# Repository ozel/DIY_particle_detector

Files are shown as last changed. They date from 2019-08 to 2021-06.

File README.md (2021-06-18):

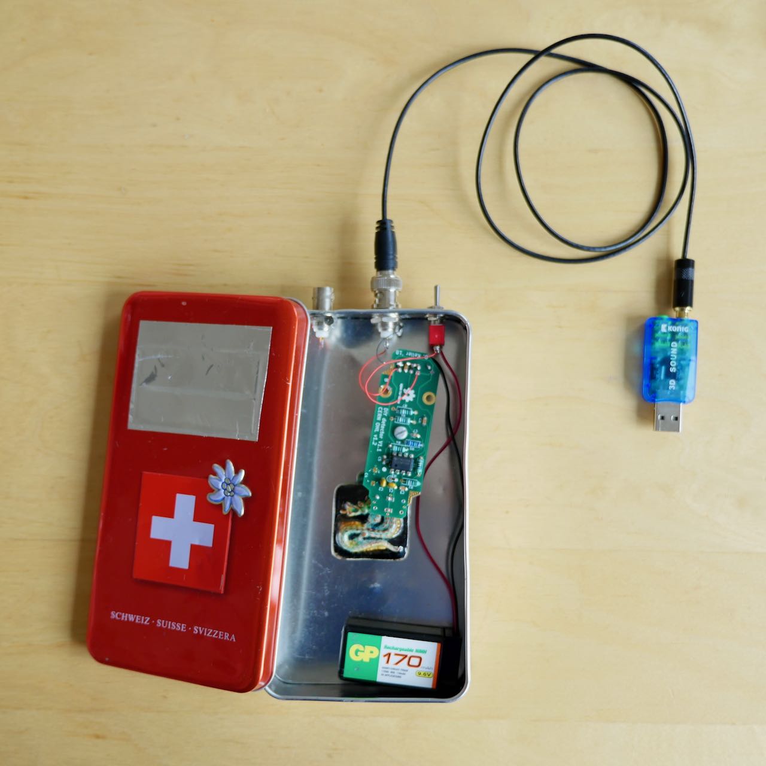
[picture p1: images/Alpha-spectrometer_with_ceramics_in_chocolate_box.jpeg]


*Corresponding scientific article:* 

*Repository archive on Zenodo:* 

# DIY Particle Detector

**Short summary video on twitter**<br>
:point_right: https://twitter.com/CERN/status/1260600298206302210

A mobile low-cost spectrometer for measuring ionising radiation like alpha particles and electrons (energy range: 33 keV to 8 MeV).   
It's an experimental educational tool and citizen science device made for exploring natural and synthetic sources of radioactivity such as stones, airborne radon, potassium-rich salt or food and every-day objects (Uranium glass, ceramics, old Radium watches etc.).

<u>*The main project documentation can be found in **[the Wiki](https://github.com/ozel/DIY_particle_detector/wiki)**.*</u>   

A summary of the main aspects can be found below.    
The hardware design and documentation is licenced under the [CERN Open Hardware License](https://github.com/ozel/DIY_particle_detector/blob/master/hardware/V1.2/CERN_OPEN_HARDWARE_LICENSE_OHL_v_1_2.txt).   
The open source software is provided under the terms of the [BSD licence](https://github.com/ozel/DIY_particle_detector/blob/master/LICENSE).

This project received funding and support by [CERN](http://home.cern) and the [Fellow FreiesWissen program](https://github.com/ozel/DIY_particle_detector/wiki/Fellow-FreiesWissen-Project).

 &#8195;    

***Project Overview:***
* [How does it work?](#how-does-it-work)
* [Hardware](#hardware)
    * [Two variants](#detector-variants): Electron-Detector (easier, lower costs) and Alpha-Spectrometer (more advanced)
    * [General requirements](#general-requirements)
    * [Detector signals](#detector-signals)
* [Software](#software) for recording and analysing measurements
* [Reference measurements and plots](#reference-measurements-and-plots)
* [Workshops](#workshops) with high-school students, teachers and makers

*Much more detailed information is available in **[the project Wiki](https://github.com/ozel/DIY_particle_detector/wiki)**.*     

## How does it work?
Tiny amounts of electrical charge are generated in repurposed photodiodes by impinging particles. The charges form currents which are amplified and converted into voltage pulses that are compatible with audio/microphone signal inputs.
The size of the pulse is proportional to the energy deposited by the ionising radiation. A reference calibration with sources of known energy spectra is provided.

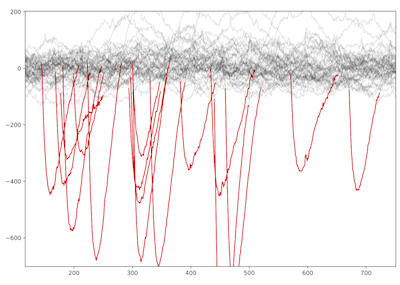
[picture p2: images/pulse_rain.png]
<br><br>

A superposition of several recorded pulse waveforms from electrons of beta decays (KCl salt sample, more info below) is shown on the right. This is the raw analog ouput signal of the detector.

Black lines in the upper area represent electronic noise, detected signal pulses from the natural radioactivity of potassium (isotope K-40) are highlighted in red.

<br>

<br>

<br>

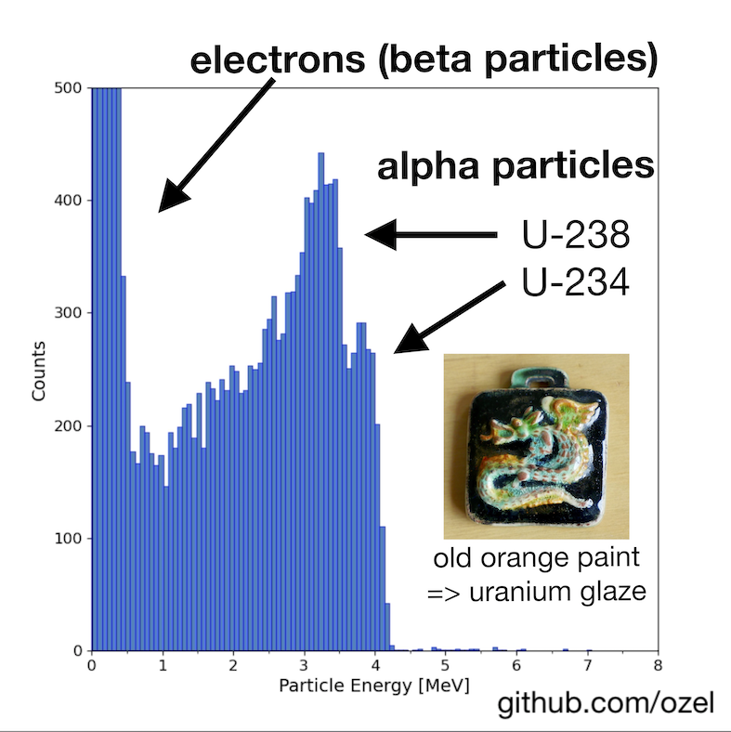
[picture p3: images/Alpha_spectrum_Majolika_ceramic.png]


The energy spectrum on the right - derived from the size of signal pulses - was taken from an old ceramics pendant of the Majolika manufacture (Karlsruhe/Germany) - without vacuum pump, in normal ambient air! 

The characteristic alpha energies of the uranium isotopes are about 1 MeV lower than the actual values due to internal absorption caused by the transparent surface coating on top of the orange uranium-based glaze. More details on the energy calibration below and in the [paper](https://doi.org/10.3390/s19194264).

<br>

<br>

## Hardware

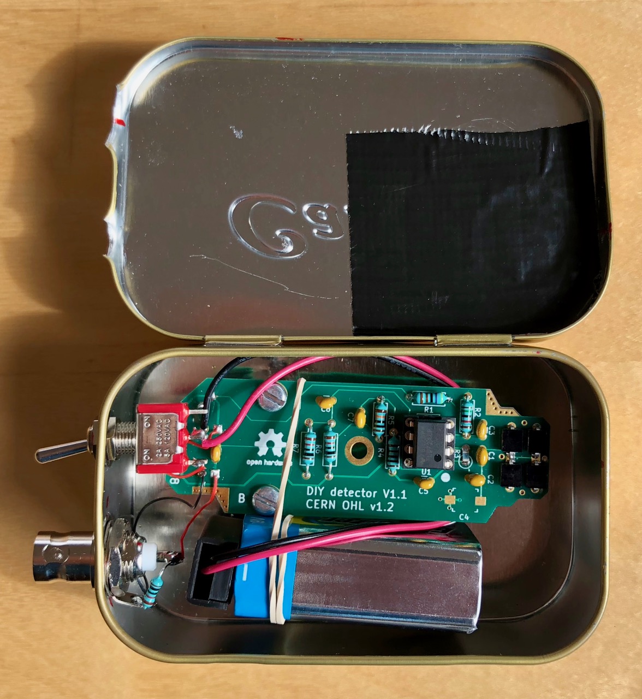
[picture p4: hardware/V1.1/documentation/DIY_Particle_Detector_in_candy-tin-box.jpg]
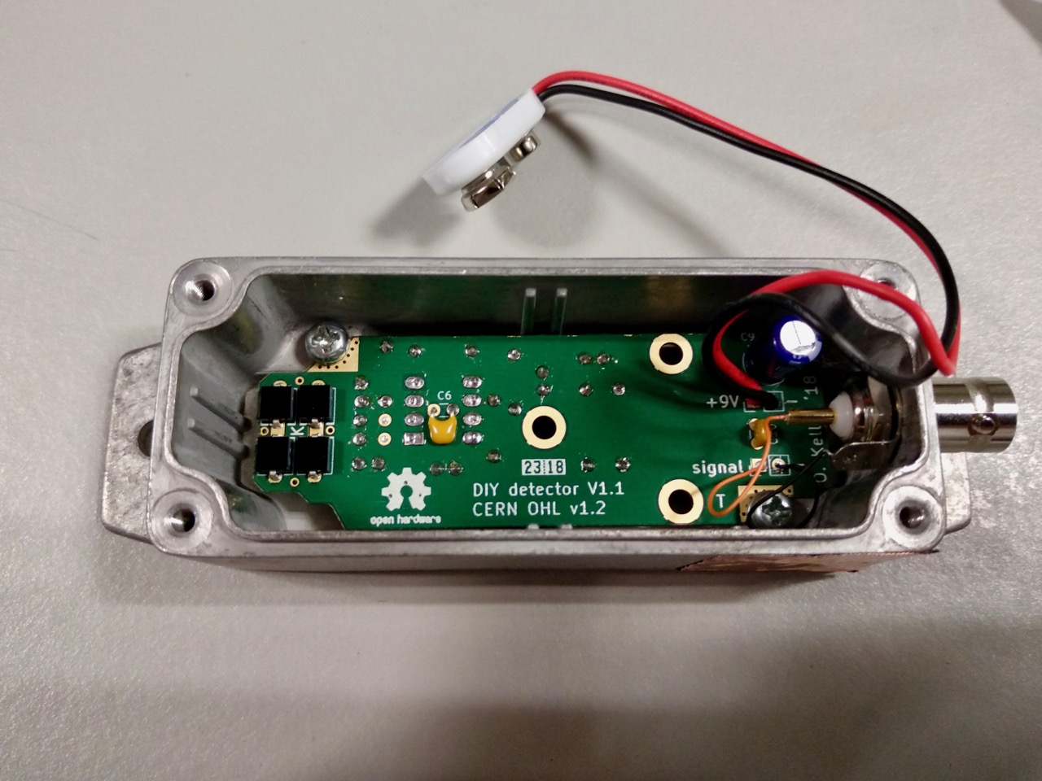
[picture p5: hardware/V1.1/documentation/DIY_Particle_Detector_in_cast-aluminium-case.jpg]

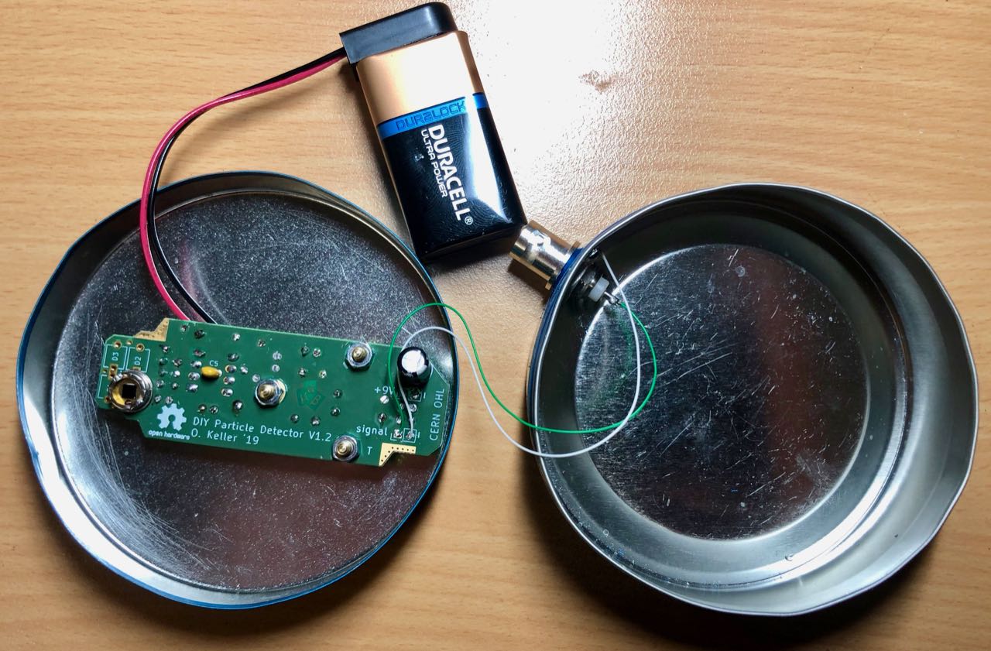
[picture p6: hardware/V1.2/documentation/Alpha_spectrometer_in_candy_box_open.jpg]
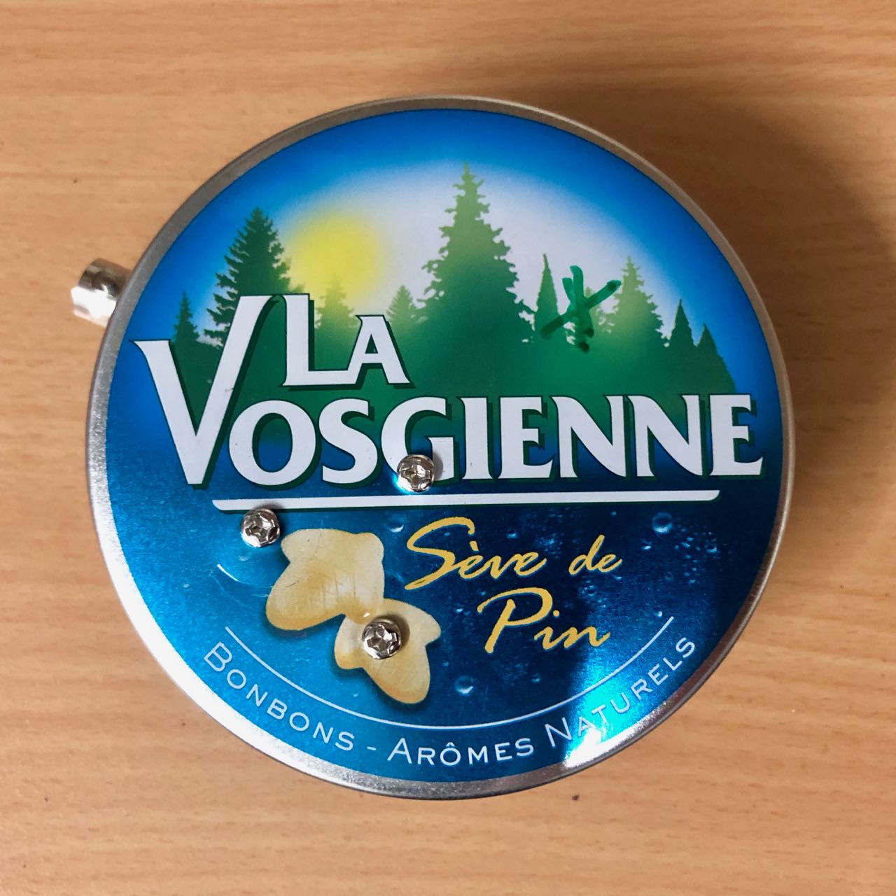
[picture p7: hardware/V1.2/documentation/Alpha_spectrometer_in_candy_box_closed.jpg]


More photos of finished builds from users around the world can be found in the [picture gallery](https://github.com/ozel/DIY_particle_detector/wiki/Gallery).     
The open hardware design in this repository is released under the terms of the CERN Open Hardware Licence V1.2.
Usage guidelines and legal requirements for users of this license can be found [here](https://ohwr.org/project/cernohl/wikis/Documents/CERN-OHL-version-1.2).
### Detector Variants
The same circuit board is used with two partially different sets of components in two assembly variants.
For electronic beginners, starting with the electron-detector version is *highly recommended* over the alpha-spectrometer.

* ***Alpha-spectrometer*** measuring energies of alpha particles and electrons using one BPX61 diode.<br/>
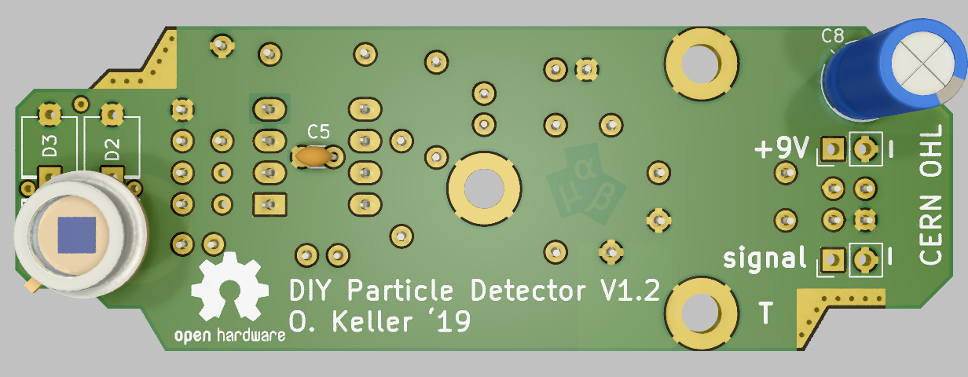
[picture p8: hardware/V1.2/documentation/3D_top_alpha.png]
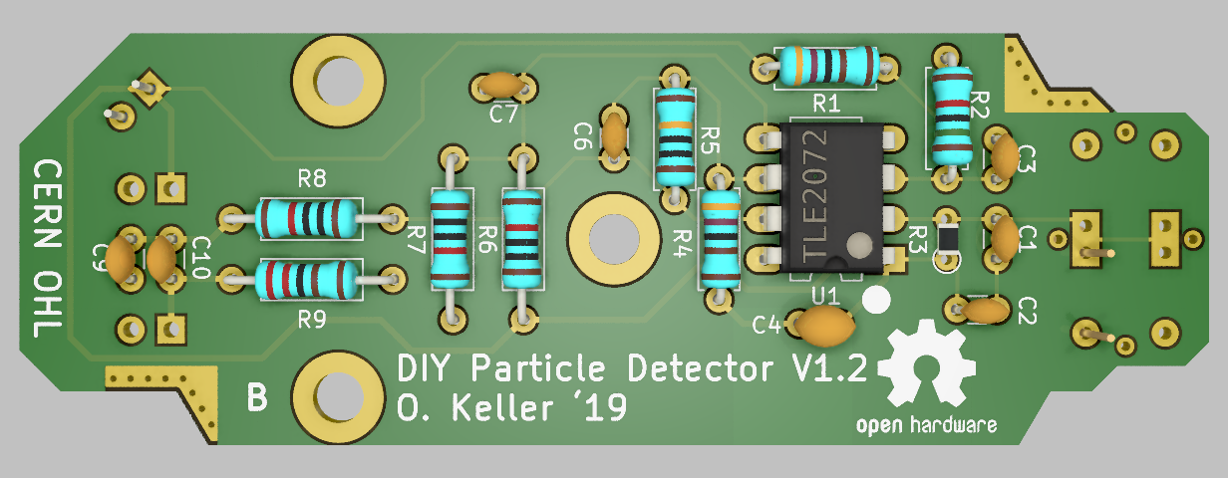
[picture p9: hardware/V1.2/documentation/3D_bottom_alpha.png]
  <br/>
  After the glass window of the diode is carefully broken-up and removed, it can sense alpha particles (see close-up pictures in the [wiki](https://github.com/ozel/DIY_particle_detector/wiki/Diodes#preparation-of-the-bpx61-diode-for-alpha-spectroscopy). 
  The circuit works most precise with only one BPX61 diode (lowest electronic noise) and was specificaly tuned for this scenario.
  * [get alpha-spectrometer parts & circuit board via kitspace](https://kitspace.org/boards/github.com/ozel/diy_particle_detector/diy%20alpha%20spectrometer/)
  * [short parts overview & assembly guide for the alpha-spectrometer](https://raw.githubusercontent.com/ozel/DIY_particle_detector/master/hardware/V1.2/documentation/DIY%20detector%20-%20parts%20overview%20v1-2%20alphaspectrometer%20version.pdf)
  * [detailed assembly instructions and list of required tools](https://github.com/ozel/DIY_particle_detector/wiki/Assembly-Instructions)
  * [scientific article incl. reference energy calibration with alpha sources](https://doi.org/10.3390/s19194264)

* ***Electron/beta radiation detector*** measuring mostly electrons (plus few gamma photons) with four very low-cost BPW34F or BPW34FA diodes (<1 EUR each).<br/>
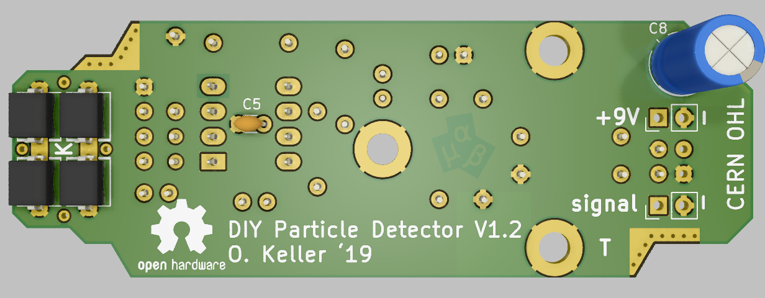
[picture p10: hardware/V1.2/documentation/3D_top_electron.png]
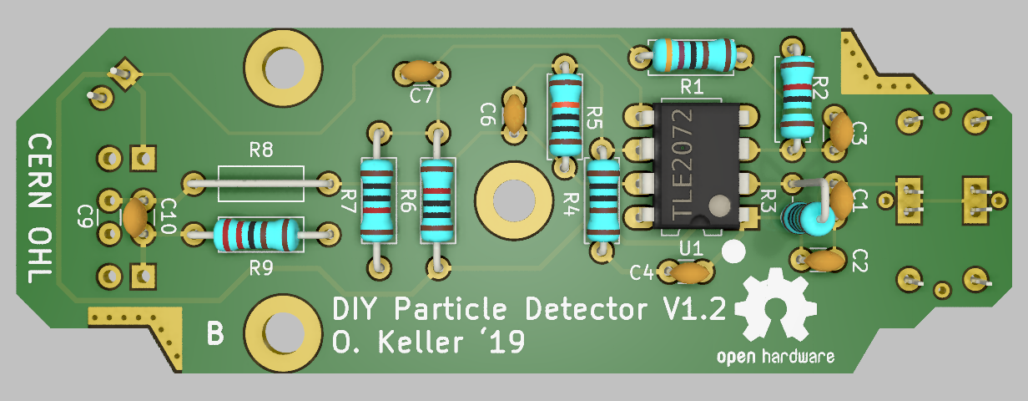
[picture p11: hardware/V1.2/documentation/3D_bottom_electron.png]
  <br/>
  This variant is not able to detect alpha particles but is  easier to operate (less sensitive to visible light and electromagnetic interference, see section on general requirements below). It is also more sensitive towards sources of low intensity (low rate of radioactive decays) since it has four times the sensor volume compared to using only one diode as sensor. This version is ideal for beginners, in total only 8 components are different compared to the alpha-spectrometer variant above. This variant is similar to the previous circuit version 1.1.
  * [get electron-detector parts & circuit board via kitspace](https://kitspace.org/boards/github.com/ozel/diy_particle_detector/diy%20electron%20detector/)
  * [short parts overview & assembly guide for the electron-detector](https://raw.githubusercontent.com/ozel/DIY_particle_detector/master/hardware/V1.2/documentation/DIY%20detector%20-%20parts%20overview%20v1-2%20electron%20version.pdf) 
  * [detailed assembly instructions and list of required tools](https://github.com/ozel/DIY_particle_detector/wiki/Assembly-Instructions)

Both kinds of diodes, the BPW34 series in various plastic cases and the BPX61 with metal casing, have the same sensitive area (~7 mm^2). The physics of these sensors when used with ionizing radiation is explained in detail in the [article corresponding to this repository](https://doi.org/10.3390/s19194264). The section about figure 1 discusses why their efficiency for detecting gamma photons is quite low in general.  

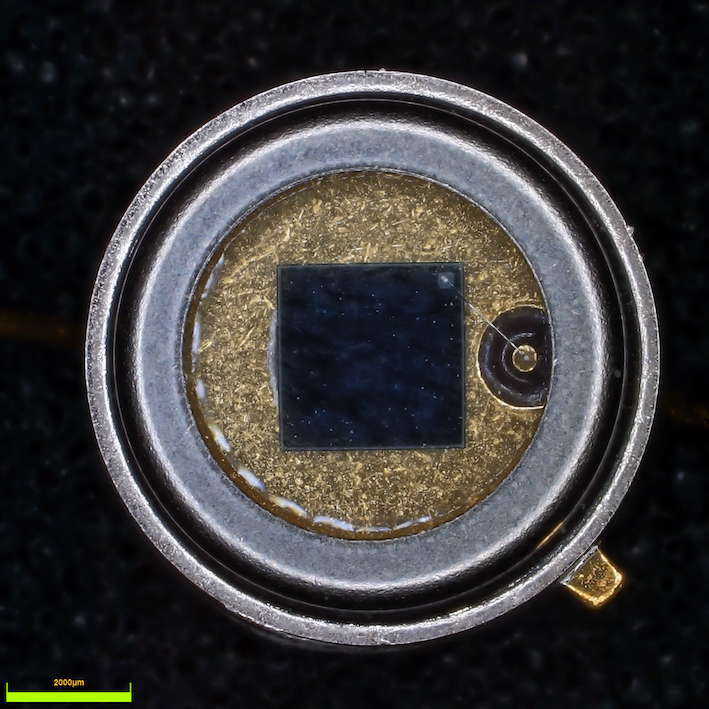
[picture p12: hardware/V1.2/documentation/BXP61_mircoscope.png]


Mircoscope image of the Osram BPX61 diode on the left, the green scale indicates 2 mm. The sensitive area of the silicon chip is 2.65 x 2.65 mm^2. A bond wire from the anode pin on the right connects the top of the silicon chip (this side is also marked with a notch in the metal case, lower right corner). For detecting alpha particles, the glass window of this diode must be removed.    
Further instructions in the [wiki](https://github.com/ozel/DIY_particle_detector/wiki/Diodes).

<br>

<br><br>

<br><br>

### General Requirements

* An absolutely light-tight and electromagnetically shielding metal case is mandatory. Either a commercial one made of die casted aluminium (thick metal provides better immunity towards vibrations and prevents "microphonic effects") or an upcycled tin box for candies. Detailed recommendations in the [wiki](https://github.com/ozel/DIY_particle_detector/wiki/Enclosures).
* 9 V [battery](https://github.com/ozel/DIY_particle_detector/wiki/Batteries). NIMH-type accumulators with a nominal value of 9.6 V work best (mains-connected power supplies would introduce too much noise, always use batteries if building the detector for the first time!)
* Signal output is in the range of +/- 0.1 V and compatible with an audio/microphone input such as a [headset connector](https://github.com/ozel/DIY_particle_detector/wiki/Cables#connection-with-a-headset-socket) of a mobile phone or laptop (or an oscilloscope if available)
* The alpha-spectrometer should be operated using a low-cost USB soundcard for best results, see the [wiki](https://github.com/ozel/DIY_particle_detector/wiki/Soundcards).
* The connection cable should be shielded and not too long, recommendations in the [wiki](https://github.com/ozel/DIY_particle_detector/wiki/Cables). 

### Detector Signals
Typical signals from the electron-detector (left/top) and alpha-spectrometer (right/bottom) on an oscilloscope:
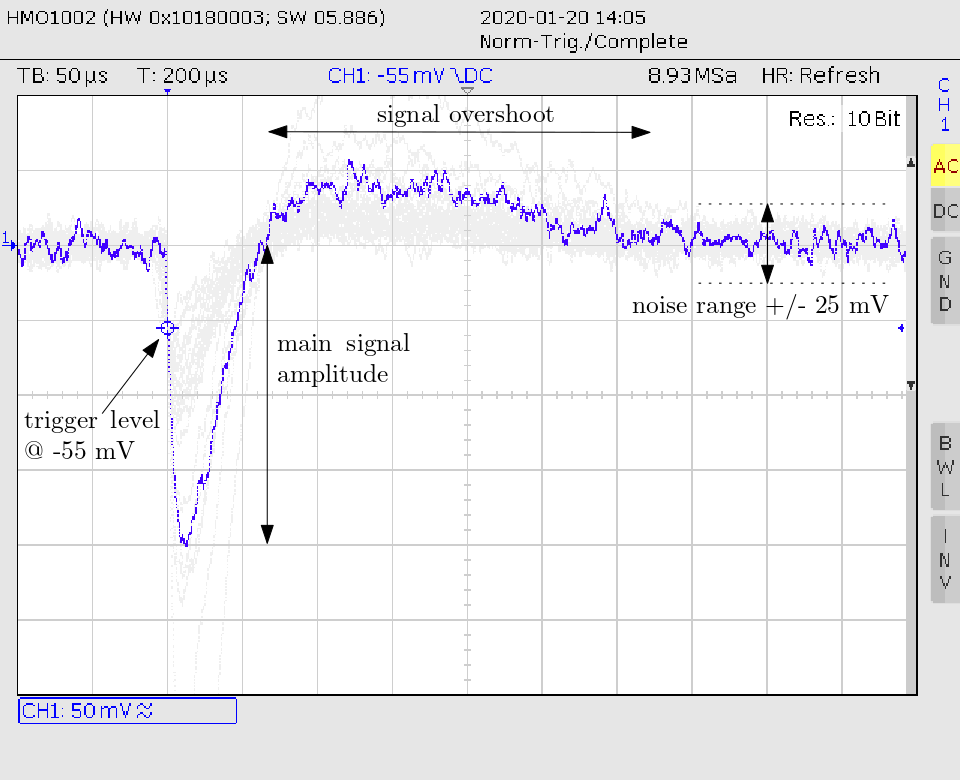
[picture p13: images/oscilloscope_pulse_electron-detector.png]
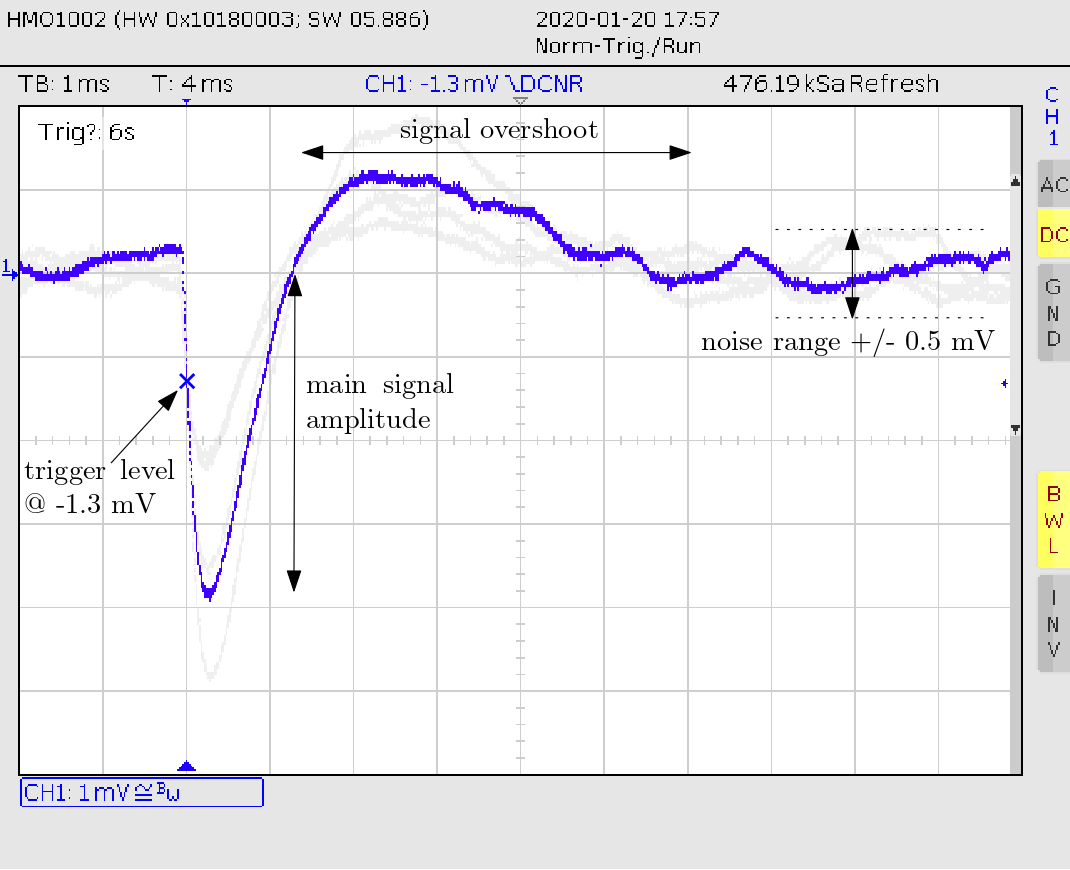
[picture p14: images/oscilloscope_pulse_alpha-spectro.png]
      
More details in the [wiki](https://github.com/ozel/DIY_particle_detector/wiki/Oscilloscope-Measurements).

## Software
The open source software in this repository is provided under the terms of the BSD Licence.

It consists of two parts (links to the wiki):
* [Recording, real-time display and counting of particle pulses](https://github.com/ozel/DIY_particle_detector/wiki/Software#signal-display--pulse-counting)     
  Different softwares for desktop computers as well as mobile devices are decsribed in the wiki.     
  Most universal is a [web browser application](https://ozel.github.io/DIY_particle_detector/data_recording_software/webGui/) based on the Web Audio API available in modern browsers (recent Chrome and Firefox versions work best):     
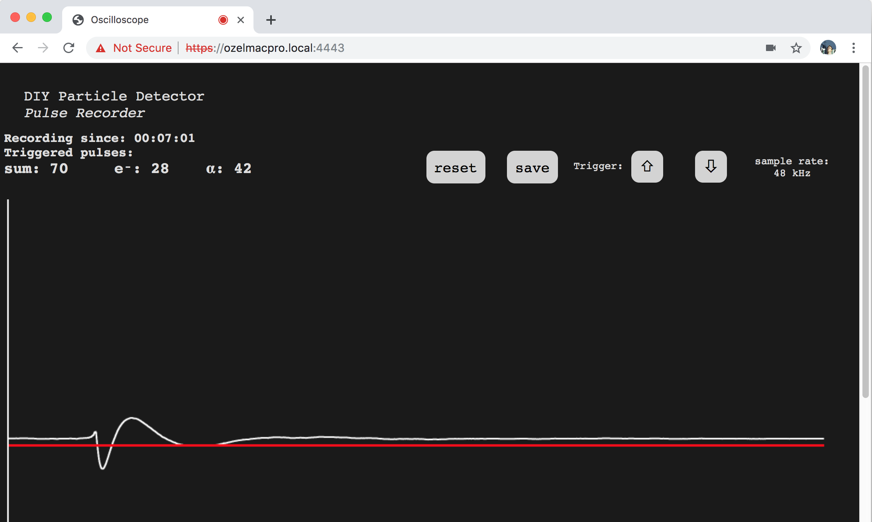
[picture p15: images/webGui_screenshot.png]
A single pulse recorded by the web browser GUI.
        
  This acts essentially as a software oscilloscope with trigger functionality (red line = trigger level) reading small detector pulses directly from the microphone input or headset socket of a computer or mobile device.

* [Data analysis of alpha-spectrometer measurements](https://github.com/ozel/DIY_particle_detector/wiki/Software#energy-spectra-from-alpha-particles), providing calibrated energy spectra and time series histograms

## Reference measurements and plots

Several reference measurements have been taken and stored in [data_analysis_and_reference_measurements/diode_detector/data](https://github.com/ozel/DIY_particle_detector/tree/master/data_analysis_and_reference_measurements/diode_detector/data). All have been recorded using the very low-cost [CM108 USB soundcard](https://github.com/ozel/DIY_particle_detector/wiki/Soundcards), sampling the input signal @ 48 kHz and 16-bit resolution.     
*If this whole respoitory is cloned using git, the [git LFS](https://help.github.com/en/articles/duplicating-a-repository#mirroring-a-repository-that-contains-git-large-file-storage-objects) extension must be used to get as well the large data files (~ 1 GB).*
Alternatively, the data files can be downloaded from this [Zenodo data archive](https://doi.org/10.5281/zenodo.3361764).

Overview on reference measurements:

* A mixed alpha source featuring Gd-148, Pu-239, Am-241 & Cm-244 with a combined alpha energy spectrum of 3 to 6 MeV
* 10 g of KCl (potassium chlorid) salt (an alternative to NaCl table salt) as an example for detection of electrons from beta-decays (from naturally occuring K-40)
* a small columbite stone (containing trace amounts of uranium ore), a combined source of electrons and alphas (and gamma photons which do not interact enough within the thin diode detector to be relevant)
* a watch hand from an old watch that was painted with luminescent radium paint. Featuring Ra-226 and all it's radioactive progeny isotopes

## Workshops

These DIY particle detectors have been built by high school students (age 16 - 18), teachers, makers, and citizen science enthusiasts (age ~20 - 60) during several workshops.
After a little introduction into the soldering of electronic components, the whole device can be built in less than two hours - including the modification of a candy tin box as its case.

* [S'Cool LAB Summer Camp 2017](https://indico.cern.ch/event/570855/timetable/) at CERN, [poster presentation](https://indico.cern.ch/event/570855/contributions/2616929/attachments/1504724/2344411/RG3_DIY_Detector.pdf)
* [Student Summer School of Barcelona Technoweek 2017](http://icc.ub.edu/congress/TechnoWeek2018/outreach_EN.php), [CERN news](https://home.cern/news/news/knowledge-sharing/summer-school-secondary-students-spain)
* [S'Cool LAB Summer Camp 2018](https://indico.cern.ch/event/726779/timetable/) at CERN, [poster presentation, page 3](https://indico.cern.ch/event/726779/contributions/2991390/attachments/1697186/2732121/pdfjoiner.pdf)
* [Gathering of Open Science Hardware 2018 in Shenzhen China](http://openhardware.science/gatherings/gosh-2018-2/), [workshop documentation](https://forum.openhardware.science/t/day-3-build-your-own-particle-detector-discover-natural-radioactivity/1468)

*Notes and announcements of future workshops can be found in the **[Wiki](https://github.com/ozel/DIY_particle_detector/wiki)**.*     

---

The [Pixel Detector](https://github.com/ozel/DIY_particle_detector/wiki/Pixel-Detectors) and [Diode Characterisation](https://github.com/ozel/DIY_particle_detector/wiki/Diode-Characterisation) sections have been moved to the [wiki](https://github.com/ozel/DIY_particle_detector/wiki) of this project. Both are related to the [scientific article](https://www.mdpi.com/1424-8220/19/19/4264/htm) and represent supplementary material.

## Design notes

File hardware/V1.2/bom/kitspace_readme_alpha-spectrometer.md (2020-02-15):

# DIY Particle Detector
## Alpha-Spectrometer Variant

This open hardware project is a mobile low-cost spectrometer for measuring ionising radiation like alpha particles and electrons (energy range: 33 keV to 8 MeV).
It's an educational tool and citizen science device made for exploring natural and synthetic sources of radioactivity such as stones, airborne radon, potassium-rich salt or food and every-day objects (Uranium glass, old Radium watches etc.).

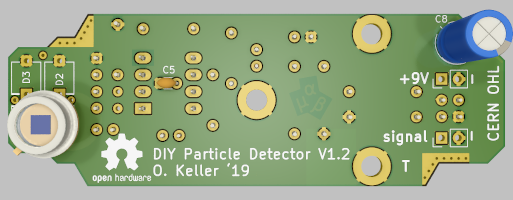
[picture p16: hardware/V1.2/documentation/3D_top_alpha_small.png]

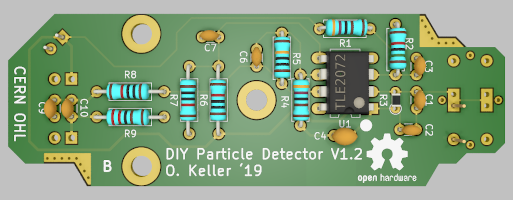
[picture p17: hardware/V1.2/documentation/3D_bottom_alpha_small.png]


[Parts overview and assembly guide](https://github.com/ozel/DIY_particle_detector/blob/master/hardware/V1.2/documentation/DIY%20detector%20-%20parts%20overview%20v1-2%20alphaspectrometer%20version.pdf)

The other [electron-detector variant](https://kitspace.org/boards/github.com/ozel/diy_particle_detector/diy%20electron%20detector/) of this project is easier to operate but cannot measure alpha particles.
Both versions of the DIY Particle Detector are using the same circuit board with different sets of components.

Please refer to the [main project description](https://github.com/ozel/DIY_particle_detector/) for further details.

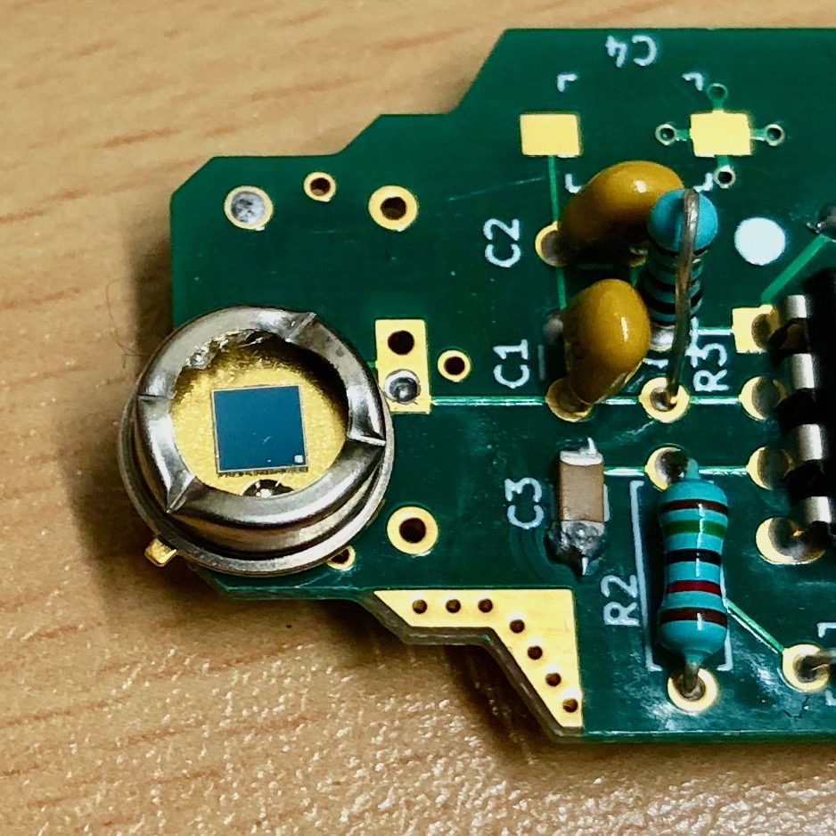
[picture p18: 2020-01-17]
hardware/V1.2/documentation/BPX61_onboard.jpg

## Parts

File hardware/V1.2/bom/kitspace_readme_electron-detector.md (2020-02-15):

# DIY Particle Detector 
## Electron-Detector Variant

This open hardware project is a mobile low-cost detector for measuring 
ionising radiation like electrons from beta radiation (plus some gamma photons).
It's an educational tool and citizen science device made for exploring 
natural and synthetic sources of radioactivity such as stones, airborne radon, 
potassium-rich salt or food and every-day objects (Uranium glass, old Radium watches etc.).

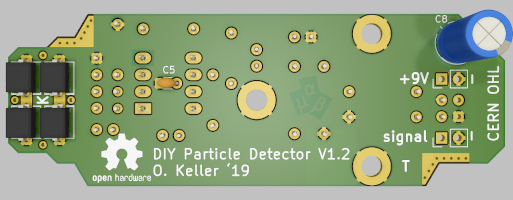
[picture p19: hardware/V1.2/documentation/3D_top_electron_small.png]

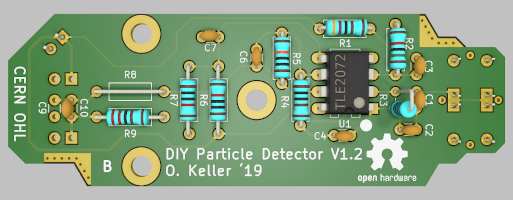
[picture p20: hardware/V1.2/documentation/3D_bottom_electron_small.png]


[Parts overview and assembly guide](https://github.com/ozel/DIY_particle_detector/blob/master/hardware/V1.2/documentation/DIY%20detector%20-%20parts%20overview%20v1-2%20electron%20version.pdf)

The other [alpha-spectrometer variant](https://kitspace.org/boards/github.com/ozel/diy_particle_detector/diy%20alpha%20spectrometer) of this 
project can measure the energy spectrum of alpha particles but is more difficult 
to operate. Both versions of the DIY Particle Detector are using the same circuit board with different sets of components.

Please refer to the [main project description](https://github.com/ozel/DIY_particle_detector/) for further details.

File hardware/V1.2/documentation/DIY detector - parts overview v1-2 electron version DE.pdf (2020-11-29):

## DIY Teilchendetektor

Bauteileübersicht - Elektronen-Detektor Variante mit vier Dioden

Widerstände, Werte in Ohm: | Kondensatoren, Werte in Farad:
R1 | 4.7 kΩ (4k7) | C1, C2, C6 | 10 pF
gelb lila schwarz braun (braun) | Markierung: 100
R2 | 15 kΩ | C3, C4, C5, C7, C10 | 100 nF

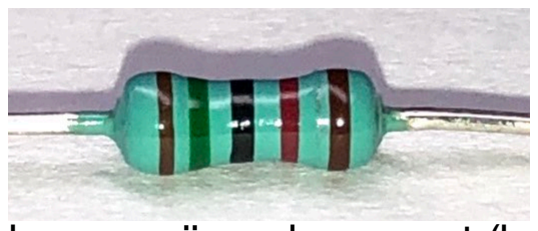
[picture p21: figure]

braun grün schwarz rot (braun) | Markierung: 104
R3 | 10 MΩ | C8 | 47 µF
braun schwarz schwarz grün (braun) | Polarität: kurzer pin = -, langer pin = +
R4 | 1 kΩ | C9 wird nicht benötigt in dieser Variante (auslassen und nicht bestücken)
| | D1 - D4, Silizium PIN Diode BPW34 (F)
braun schwarz schwarz braun (braun)
R5 | 100 kΩ

braun schwarz schwarz orange (braun)

R6, R7 10 kΩ

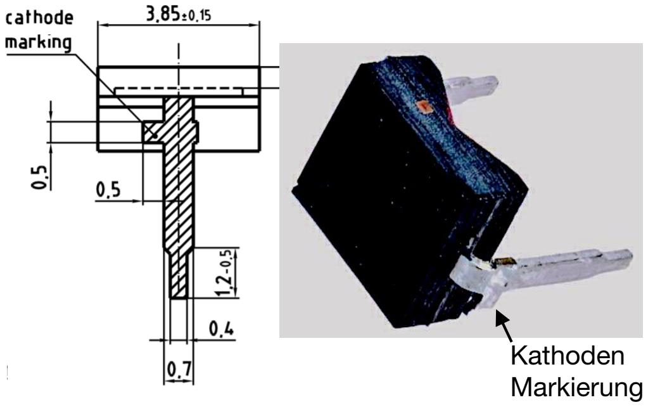
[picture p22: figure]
Kathoden Markierung

Polarität: Pin mit Ausbuchtung = Kathode

braun schwarz schwarz rot (braun) U1, Operationsverstärker TLE2072
R8 wird durch ein Stück Draht ersetzt (0 Ohm)
R9 | 2.2 kΩ (2k2)

rot rot schwarz braun (braun)

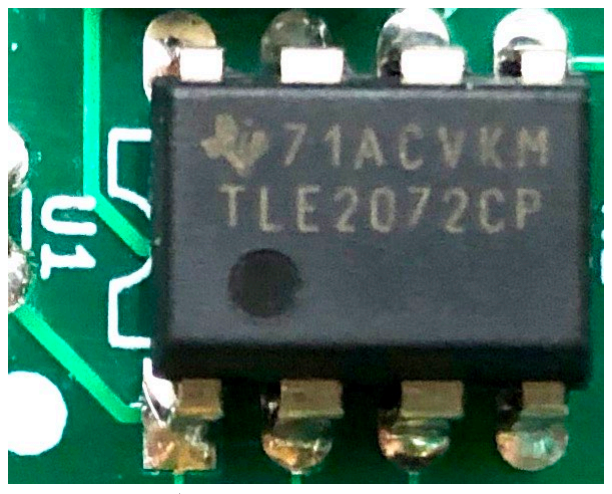
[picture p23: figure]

Pin 1 auf Platine & Chip per Kreis markiert

### Bauanleitung

Generell: Die kleinsten Teile zuerst einlöten, die größten am Schluß.

1. Alle Widerstände an den richtigen Stellen einlöten, Farbbänder mit Bildern vergleichen.
- R3 muss senkrecht eingelötet werde, die übrigen flach und parallel zur Platine
- R8 wird durch ein kurzes Stück Draht ersetzt
- Drähte der Widerstände nach dem Löten so kurz wie möglich abschneiden
2. Die kleinen Kondensatoren C1 bis C7 und C10 einlöten.
- C9 bleibt frei, der große C8 kommt später
- Drähte der Kondensatoren nach dem Löten so kurz wie möglich abschneiden
3. Die vier BPW34 Dioden einlöten.
- korrekte Polarität der Dioden sorgfältig an Hand der Bilder überprüfen
- Kathoden-Pin mit Ausbuchtung muss zum 'K'-Symbol in der Mitte der Platine zeigen
- Drähte der Dioden nach dem Löten so kurz wie möglich abschneiden
4. Den schwarzen Verstärkerchip U1 einlöten, nachdem die Pins gerade gebogen wurden.
- korrekte Polarität des Chips sorgfältig an Hand der Bilder überprüfen
5. Den großen Kondensator C8 einlöten, die Platinenseite mit genug Platz dafür wählen.
- Abhängig vom Gehäuse, kann die nicht markierte Seite besser geeignet sein.
- korrekte Polarität des Kondensators sorgfältig an Hand der Bilder überprüfen
- Drähte des Kondensators nach dem Löten so kurz wie möglich abschneiden
6. Falls ein Multimeter zur Hand ist: Widerstand am Batterieanschluß messen (+9V und -).
- Wenn der Widerstand nicht 9-10 kΩ beträgt, gibt es ein Problem im Aufbau.
7. Den Batterie-Clip an Schalter und die Platine löten wie unten zu aufgezeichnet.
- kurzes rotes Kabelstück vom Clip abschneiden, Schalter und Platine damit verbinden
8. Die Platine mit ein oder zwei Schrauben im Gehäuse befestigen.
9. Den Schalter und BNC Signal-Stecker in Löchern am Metallgehäuse verschrauben.
10. Signal & Masse (-) durch zwei weitere Kabelstücke mit dem Signal-Stecker verlöten.
11. Eine volle 9 Volt Batterie verbinden, in das Gehäuse legen. Deckel gut verschließen!
- Umgebungslicht darf nicht in's Innere gelangen, zur Not mit Kleidungsstück abdecken
12. Verbinde ein Oszilloskop oder Smartphone/Laptop zum Messen, mehr dazu im Wiki.

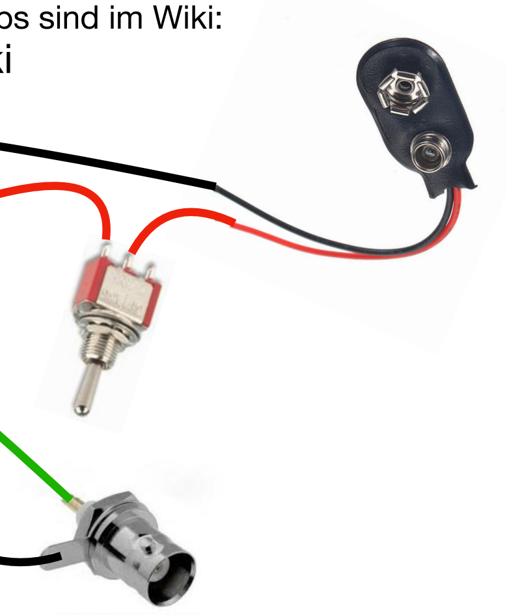
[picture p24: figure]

Eine detailiertere Bauanleitung und Troubleshootingss Tips sind im Wiki:

### www.github.com/ozel/DIY_particle_detector/wiki

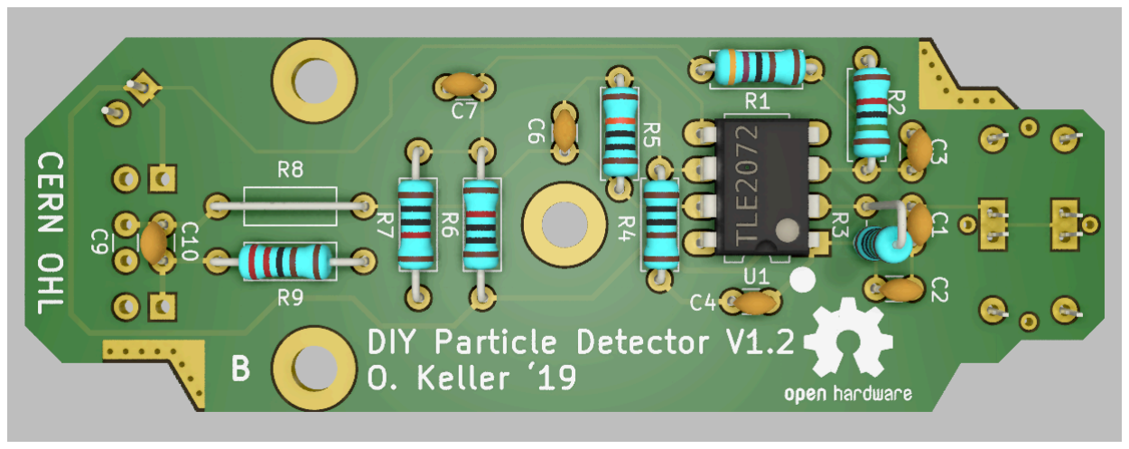
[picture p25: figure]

DIY Particle Detector V1.2 CERN Open Hardware Licence Oliver Keller, November 2020

‘K’ =

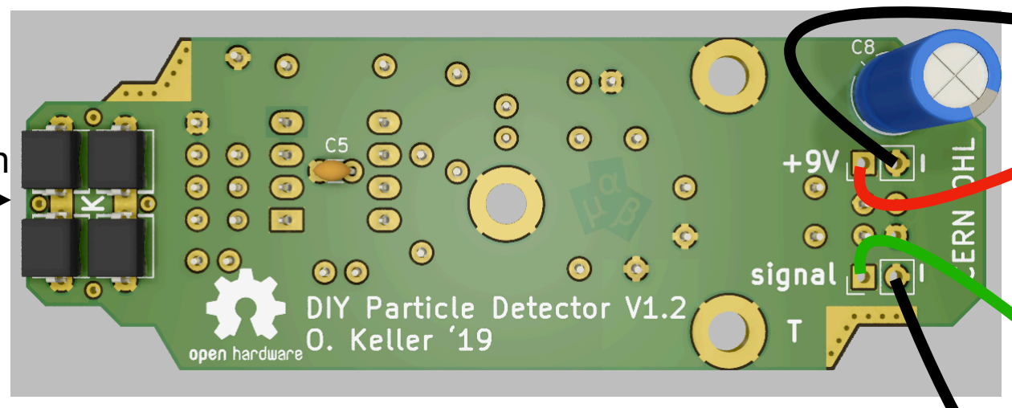
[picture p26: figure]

Kathoden

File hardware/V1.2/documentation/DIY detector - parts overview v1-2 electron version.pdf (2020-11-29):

## DIY Particle Detector

Parts Overview - Electron-Detector Variant with four Diodes

Resistors, values in Ohm: | Capacitors, values in Farad:
R1 | 4.7 kΩ (4k7) | C1, C2, C6 | 10 pF
yellow purple black brown (brown) | marking: 100
R2 | 15 kΩ | C3, C4, C5, C7, C10 | 100 nF


brown green black red (brown) | marking: 104
R3 | 10 MΩ | C8 | 47 µF
brown black black green (brown) | polarity: short pin = minus, long pin = plus
R4 | 1 kΩ | C9 is not needed in this variant (leave empty and do not populate)
| | D1 - D4, Silicon PIN Diode BPW34 (F)
brown black black brown (brown)
R5 | 100 kΩ

brown black black orange (brown)

R6, R7 10 kΩ

cathode marking

polarity: pin with notch = cathode

brown black black red (brown) U1, Dual operational amplifier TLE2072 R8 must be shorted with a wire (0 Ohm)

R9 | 2.2 kΩ (2k2)

red red black brown (brown)


pin 1 on board & chip marked with a circle

### Assembly Instructions

In general: Start with the smallest parts and solder the largest ones at the end.

1. Solder all resistors in the right place, compare their color bands with the pictures.
- R3 must be soldered upright, the others stay flat and parallel to the board
- R8 shall be just shorted with a piece of wire
- cut all resistor leads after soldering as short as possible
2. Solder the small capacitors C1 to C7 and C10.
- C9 shall be skipped, the large C8 comes later
- cut all capacitor leads after soldering as short as possible
3. Solder the four BPW34 diodes in place.
- check the correct diode polarity carefully according to the pictures
- the cathode pin with the notch must face towards the ‘K’ symbol on the board center
- cut all diode pins after soldering as short as possible
4. Solder the black amplifier chip U1 in place after bending its pins straight and parallel.
- check the correct chip polarity carefully according to the pictures
5. Solder the large capacitor C8 and check on which side of the board it fits best
- choose the side of the board that has enough space available once installed in a case
- check the correct capacitor polarity carefully according to the pictures
- cut the capacitor leads after soldering as short as possible
6. If you have a multimeter: check the resistance of the battery connector (+9V and -).
- if the resistance is not around 9-10 kΩ, there is a problem that must be found
7. Solder the battery connector to the board and the switch as shown below.
- cut a short piece of wire from the battery clip and solder it between switch and board
8. Mount the board with one or two screws inside the metal enclosure.
9. Mount the switch and the BNC signal connector in holes of the metal case.
10. Solder two more wires from the signal & ground (-) connections to the BNC connector.
11. Attach a full 9 Volt battery, put it in inside the case and close the lid well!
- light must not reach inside, try covering the case with a dark piece of cloth if unsure
12. Connect an oscilloscope or smartphone/laptop for measuring, see the wiki for details.


Detailed assembly instructions and troubleshooting tips are in the wiki:

### www.github.com/ozel/DIY_particle_detector/wiki


DIY Particle Detector V1.2 CERN Open Hardware Licence Oliver Keller, November 2020

‘K’ for


cathodes

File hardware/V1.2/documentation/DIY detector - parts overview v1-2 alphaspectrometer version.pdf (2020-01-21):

DIY Particle Detector v1.2 - overview of electronic components
1-diode variant for measuring energy of alpha particles and electrons
Resistor values in Ohm: | Capacitor values in Farad:
R1, R4 | 4k7 (4.7 k) | C1, C2 | 10 p
yellow purple black brown (brown) | marking: 100
R2 | 15 k | C3, C5, C7, C10 100 n
brown green black red (brown) | marking: 104
R3 | 40 M | C4 | C6 | C9
| 470 n | 3n3 | 6n8
black SMD resistor | (474) | (332) | (682)
(SMD = Surface Mounted Device)
C8 | 47 u
R5 | 1 M

polarity: short pin= - long pin = + brown black black yellow (brown) D1 or (http://www.apple.com/uk) D4: Silicon PIN Diode BPX61: R6, R7, R8 10 k
polarity: pin
| with notch
| = anode
brown black black red (brown)
R9 | 2k2 (2.2 k)


U1 Dual Operational Amplifier: red red black brown (brown)
| | | TLE2072(A)CP
| | | polarity: circles
| | | mark position of
| | | pin 1


Check the main project description and schematic for general notes: www.github.com/ozel/DIY_particle_detector


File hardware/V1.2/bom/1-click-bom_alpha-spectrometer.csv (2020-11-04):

References | Qty | Description | Manufacturer | MPN | Manufacturer | MPN | Manufacturer | MPN | Manufacturer | MPN | Digikey | Mouser | RS | Newark | Farnell
BT1 | 1 | 9V clip | Cliff | FC6830 | Keystone | 232 | RS Pro | 489021 | Bud Industries | HH-3449 | 36-232-ND | 534232 | 489021 |  | 1650667
C1, C2 | 2 | 10pF radial 2.54mm 50V | Multicomp | MC0805N100J101A2.54MM | KEMET | C315C100J5G5TA |  |  |  |  | 399-13908-ND | 80C315C100J5G | 1463557 |  | 1694175
C3, C5, C7, C10 | 4 | 100nF radial 2.54mm 50V | Multicomp | MC0805Y104M500A2.54MM | KEMET | C320C104K1R5TA |  |  |  |  | 399-4263-ND | 80C320C104K1R | 8015404 |  | 2112751
C4 | 1 | 470nf radial 2.54mm 50V | KEMET | C320C474M5U5TA | KEMET | C320C474M5U5TA7301 |  |  |  |  | 399-13979-1-ND | 80C320C474M5U | 8015394 |  | 1457660
C6 | 1 | 3.3nF radial 2.54mm 50V | Suntan | TS170R1H332KSBBA0R | AVX | SR155C332KARTR1 | AVX | SR151C332KAR | KEMET | C315C332K1R5TA | 399-4176-ND | 581SR155C332KARTR1 | 5373606 |  | 2901293
C8 | 1 | 47uF 63V THT | Panasonic | ECA-1JHG470 |  |  |  |  |  |  | P5581-ND | 667ECA1JHG470 | 3654357 |  | 9693033
C9 | 1 | 6.8nF radial 2.54mm 50V | Suntan | TS170R1H682KSBBA0R | KEMET | C315C682K5R5TA |  |  |  |  | 399-4194-ND | 80C315C682K5R | 1463558 |  | 2901297
D4 | 1 | silicon PIN photodiode | Osram Opto | BPX 61 |  |  |  |  |  |  | 475-1350-ND | 720BPX61 | 6547785 |  | 2981630
J3 | 1 | male BNC connector | Multicomp | 13-25 | TE Connectivity | 5-1634523-1 | Adam Tech | RF1-106-D-00-50-HDW |  |  | 2057-RF1-106-D-00-50-HDW-ND | 571516345231 | 5121174 |  | 1169699
R1, R4 | 2 | 4.7k 1% axial | Multicomp | MCMF006FF4701A50 | TE Connectivity | LR1F4K7 | Vishay | MRS25000C4701FCT00 |  |  | A105962CT-ND | 279LR1F4K7 | 6833799 |  | 2401772
R2 | 1 | 15k 1% axial | Multicomp | MCMF006FF1502A50 | Vishay | MRS25000C1502FCT00 |  |  |  |  | BC4005CT-ND | 594MRS25000C1502FCT | 6833055 |  | 2401785
R3 | 1 | 40Mega 10% 0805 SMD | TE Connectivity | RH73H2A40MKTN |  |  |  |  |  |  | A106113DKR-ND | 279RH73H2A40MKTN | 2945040 |  | 1174521
R5 | 1 | 1Mega 1% axial | Multicomp | MCMF006FF1004A50 | TE Connectivity | LR1F1M0 |  |  |  |  | A105954CT-ND | 279LR1F1M0 | 149228 |  | 2330049
R6, R7, R8 | 3 | 10k 1% axial | Multicomp | MCMF006FF1002A50 | Vishay | MRS25000C1002FRP00 | TE Connectivity | LR1F10K |  |  | PPC10.0KZCT-ND | 594MRS2510K00F | 1251164 |  | 2401780
R9 | 1 | 2.2k 1% axial | Multicomp | MCMF006FF2201A50 | Vishay | MRS25000C2201FCT00 |  |  |  |  | BC4060CT-ND | 594MRS25000C2201FCT | 6833449 |  | 9466711
SW1 | 1 | SPDT switch on-none-on | Multicomp | 1MS1T1B1M1QE | TE Connectivity | A101SYZQ04 | RS Pro | 7347062 |  |  | 450-1523-ND | 506A101SYZQ04 | 7347062 |  | 9473416
U1 | 1 | TLE2072CP/ACP | Texas Instruments | TLE2072ACP | Texas Instruments | TLE2072CP |  |  |  |  | 296-10426-5-ND | 595TLE2072CP | 834156 |  | 3117961

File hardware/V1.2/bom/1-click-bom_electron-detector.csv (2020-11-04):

References | Qty | Description | Manufacturer | MPN | Manufacturer | MPN | Manufacturer | MPN | Manufacturer | MPN | Digikey | Mouser | RS | Newark | Farnell
BT1 | 1 | 9V clip | Cliff | FC6830 | Keystone | 232 | RS Pro | 489021 | Bud Industries | HH-3449 | 36-232-ND | 534232 | 489021 |  | 1650667
C1, C2, C6 | 3 | 10pF radial 2.54mm 50V | Multicomp | MC0805N100J101A2.54MM | KEMET | C315C100J5G5TA |  |  |  |  | 399-13908-ND | 80C315C100J5G | 1463557 |  | 1694175
C3, C4, C5, C7, C10 | 5 | 100nF radial 2.54mm 50V | Multicomp | MC0805Y104M500A2.54MM | KEMET | C320C104K1R5TA |  |  |  |  | 399-4263-ND | 80C320C104K1R | 8015404 |  | 2112751
C8 | 1 | 47uF 63V THT | Panasonic | ECA-1JHG470 |  |  |  |  |  |  | P5581-ND | 667ECA1JHG470 | 3654357 |  | 9693033
D1, D2, D3, D4 | 4 | silicon PIN photodiode | Osram Opto | BPW 34 FA | Osram Opto | BPW 34 F |  |  |  |  | 475-1072-ND | 720BPW34FA | 6547921 |  | 2981621
J3 | 1 | male BNC connector | Multicomp | 13-25 | TE Connectivity | 5-1634523-1 | Adam Tech | RF1-106-D-00-50-HDW |  |  | 2057-RF1-106-D-00-50-HDW-ND | 571516345231 | 5121174 |  | 1169699
R1 | 1 | 4.7k 1% axial | Multicomp | MCMF006FF4701A50 | Vishay | MRS25000C4701FCT00 | TE Connectivity | LR1F4K7 |  |  | A105962CT-ND | 279LR1F4K7 | 6833799 |  | 2401772
R2 | 1 | 15k 1% axial | Multicomp | MCMF006FF1502A50 | Vishay | MRS25000C1502FCT00 | TE Connectivity | LR1F15K |  |  | BC4005CT-ND | 594MRS25000C1502FCT | 6833055 |  | 2401785
R3 | 1 | 10Mega 1% axial | Multicomp | MCMF006FF1005A50 | Vishay | MRS25000C1005FCT00 | TE Connectivity | LR1F10M |  |  | BC3961CT-ND | 279LR1F10M | 6832945 |  | 2401834
R4 | 1 | 1k 1% axial | Multicomp | MCMF006FF1001A50 | Vishay | MRS25000C1001FCT00 | TE Connectivity | LR1F1K0 |  |  | BC3325CT-ND | 594MRS251K1%TR | 6833165 |  | 2401753
R5 | 1 | 100k 1% axial | Multicomp | MCMF006FF1003A50 | Vishay | MRS25000C1003FCT00 | TE Connectivity | LR1F100K |  |  | BC3327CT-ND | 594MRS25000C1003FCT | 6832923 |  | 2401807
R6, R7 | 2 | 10k 1% axial | Multicomp | MCMF006FF1002A50 | Vishay | MRS25000C1002FRP00 | TE Connectivity | LR1F10K |  |  | PPC10.0KZCT-ND | 594MRS2510K00F | 1251164 |  | 2401780
R9 | 1 | 2.2k 1% axial | Multicomp | MCMF006FF2201A50 | Vishay | MRS25000C2201FCT00 | TE Connectivity | LR1F2K2 |  |  | BC4060CT-ND | 594MRS25000C2201FCT | 6833449 |  | 9466711
SW1 | 1 | SPDT switch on-none-on | Multicomp | 1MS1T1B1M1QE | TE Connectivity | A101SYZQ04 | RS Pro | 7347062 |  |  | 450-1523-ND | 506A101SYZQ04 | 7347062 |  | 9473416
U1 | 1 | TLE2072CP/ACP | Texas Instruments | TLE2072CP | Texas Instruments | TL072ACP |  |  |  |  | 296-10426-5-ND | 595TLE2072CP | 834156 |  | 3117961

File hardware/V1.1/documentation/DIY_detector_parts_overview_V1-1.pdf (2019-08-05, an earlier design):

## DIY Particle Detector V1.1: Overview of Electronic Parts


Resistor values in Ohm: | Capacitors in Farad:
R1 | 4k7 (4.7 k) | C1, C2, C7 10 p

(marking: 100)

| a
yellow purple black brown (brown) | marking: 100
R2 | 15 k | C3, C5, C6, C8, C10 | 100 n
brown green black red (brown) | marking: 104
R3 | 10 M | C9 | 47 u
brown black black green (brown) | polarity: short pin = minus, long pin = plus
R4 | 1 k | D1 - D4 Silicon PIN Diode BPW34 F

brown black black brown (brown)

R5 | 100 k

brown black black orange (brown)
polarity: pin with notch = cathode
R6, R7, R8 10 k | U1 Dual operational amplifier TL072 ACP
| polarity: pin 1 marked with circle

brown black black red (brown) (R8 is optional)

cathode

pin 1

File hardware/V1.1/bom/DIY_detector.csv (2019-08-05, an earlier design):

Id | Designator | Package | Quantity | Designation | Supplier and ref
1 | R3 | R_Axial_DIN0204_L3.6mm_D1.6mm_P2.54mm_Vertical | 1 | 10M
2 | REF***,REF*** | OSHW-Logo2_9.8x8mm_SilkScreen | 2 | OSHW-Logo2_7.3x6mm_SilkScreen
3 | U1 | DIP-8_W7.62mm_LongPads | 1 | TL072
4 | C9 | CP_Radial_D6.3mm_P2.50mm | 1 | 47u
5 | C1,C2,C7 | C_Disc_D3.0mm_W1.6mm_P2.50mm | 3 | 10p
6 | C3,C5,C6,C8,C10 | C_Disc_D3.0mm_W1.6mm_P2.50mm | 5 | 100n
7 | R2 | R_Axial_DIN0207_L6.3mm_D2.5mm_P7.62mm_Horizontal | 1 | 15k
8 | R4 | R_Axial_DIN0207_L6.3mm_D2.5mm_P7.62mm_Horizontal | 1 | 1k
9 | R5 | R_Axial_DIN0207_L6.3mm_D2.5mm_P7.62mm_Horizontal | 1 | 100k
10 | R1 | R_Axial_DIN0207_L6.3mm_D2.5mm_P7.62mm_Horizontal | 1 | 4k7
11 | MK7,MK6,MK5 | MountingHole_3.2mm_M3_ISO7380_Pad | 3 | M3 support
12 | D1,D2,D3,D4 | PhotoDiode_DIL2_4.3x4.65_RM5.08 | 4 | BPW34F
13 | J1 | Pin_Header_Straight_1x02_Pitch2.54mm | 1 | BNC socket (case mounted)
14 | R6,R7 | R_Axial_DIN0207_L6.3mm_D2.5mm_P10.16mm_Horizontal | 2 | 10k
15 | BT1 | Pin_Header_Straight_1x02_Pitch2.54mm | 1 | 9V battery clip
16 | C4 | C_Trimmer_Murata_TZB4-B | 1 | ca. 10-100p
17 | MK1,MK2,MK3,MK4 | SolderWirePad_single_0-8mmDrill | 4 | via for coincidence sandwich

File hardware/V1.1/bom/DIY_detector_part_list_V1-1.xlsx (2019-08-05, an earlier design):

Reference | Value | Manufacturer | Part number | Vendor | Vendor part number | Quantity | Comment
BT1 | 9V battery clip | CLIFF | FC6830 | Farnell | 2817539 | 1
C1,C2,C7 | 10p | Multicomp | MC0805N100J101A2.54MM | Farnell | 1694175 | 3
C4 | ca. 10-100p | Murata | TZB4P400AB10R00 | Farnell | 1760637 | 1 | optional, don't populate
C3,C5,C6,C8,C10 | 100n | Multicomp | MC0805Y104M500A2.54MM | Farnell | 2112751 | 5
C9 | 47u | Panasonic | ECA1JM470 | Farnell | 9693858 | 1
D1-D4 | BPW34F | Osram/Vishay | BPW34 F(A) | Farnell | 1212740 | 4
J1 | BNC socket (case mounted) | Multicomp | 13-25 | Farnell | 1169699 | 1
R1 | 4k7 | Multicomp | MCMF006FF4701A50 | Farnell | 2401772 | 1
R2 | 15k | Multicomp | MCMF006FF1502A50 | Farnell | 2401785 | 1
R3 | 10M | Multicomp | MCMF006FF1005A50 | Farnell | 2401834 | 1
R4 | 1k | Multicomp | MCMF006FF1001A50 | Farnell | 2401753 | 1
R5 | 100k | Multicomp | MCMF006FF1003A50 | Farnell | 2401807 | 1
R6-R8 | 10k | Multicomp | MCMF006FF1002A50 | Farnell | 2401780 | 3
SW1 | wall mounted switch | Multicomp | 1MS1T1B1M1QE | Farnell | 9473416 | 1
U1 | TL072 | TI | TL072ACP | Farnell | 1103005 | 1

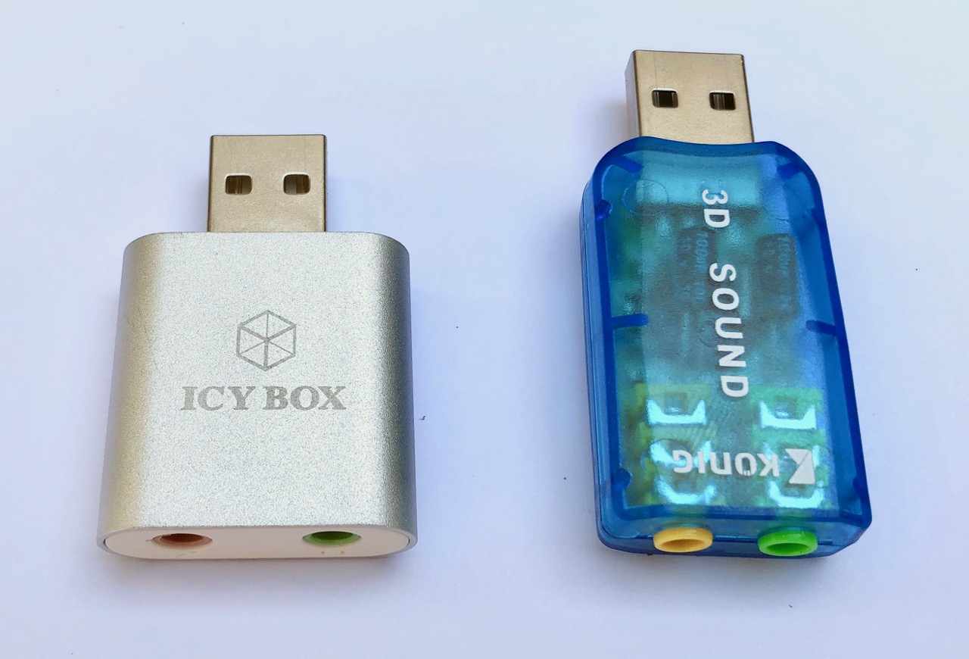
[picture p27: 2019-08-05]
images/low-cost_usb_audio_interfaces.jpg

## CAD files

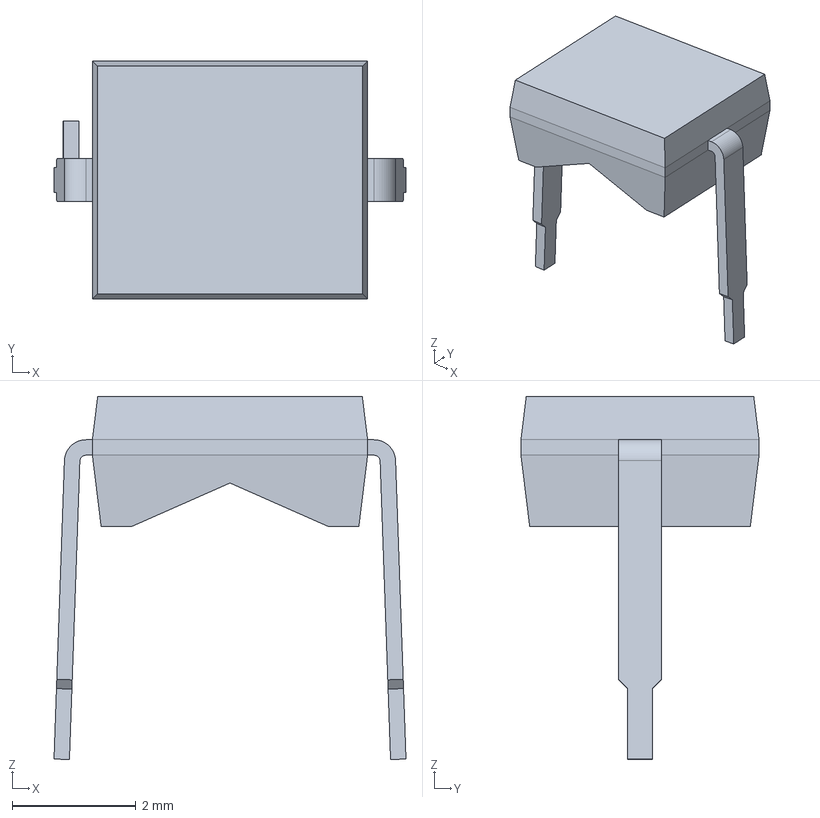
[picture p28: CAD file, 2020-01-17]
hardware/V1.2/3D/BPW34.FCStd
5.69 x 3.85 x 5.87 mm

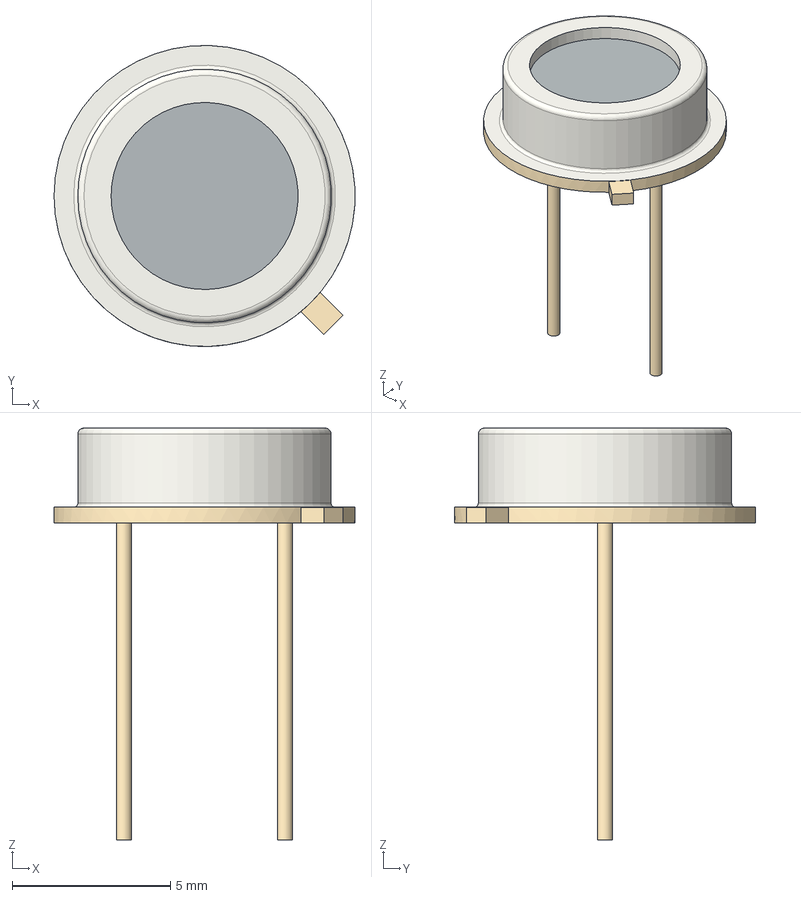
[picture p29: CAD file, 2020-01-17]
hardware/V1.2/3D/BPX61.step
9.49 x 9.50 x 13.0 mm

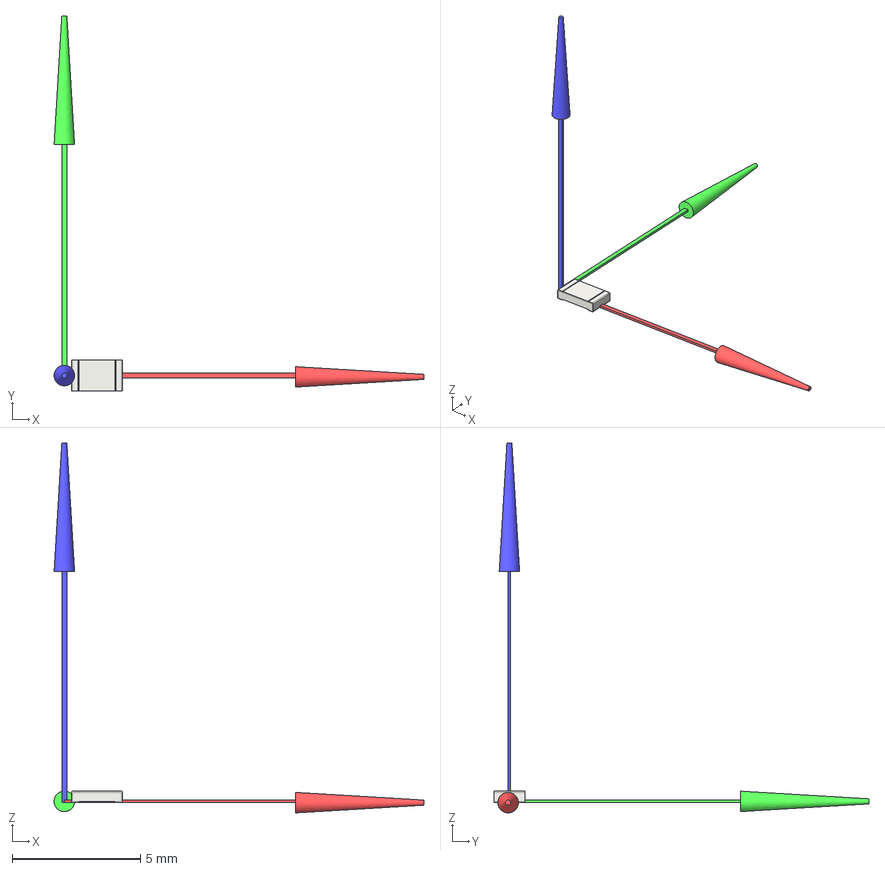
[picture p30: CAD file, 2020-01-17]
hardware/V1.2/3D/R_0805_2012Metric_THTorigin.FCStd
14.4 x 14.6 x 14.4 mm
R_0805_2012Metric_THTorigin
Z
Y
X

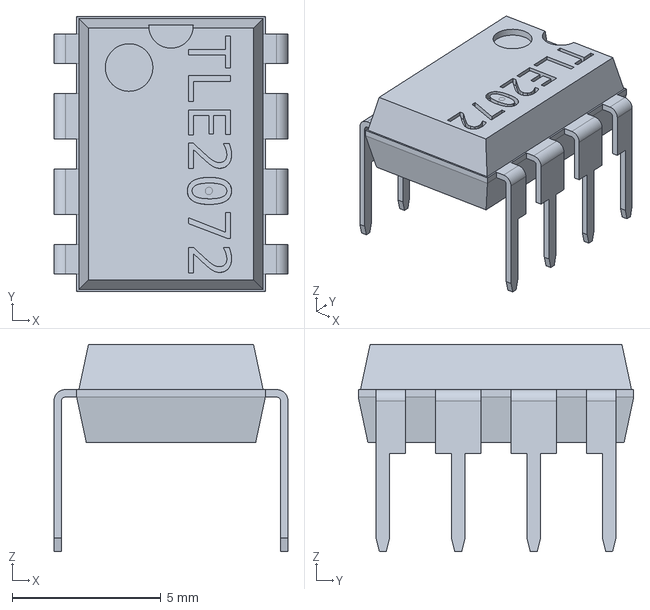
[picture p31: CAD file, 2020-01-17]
hardware/V1.2/3D/TLE2072ACP.FCStd
7.87 x 9.27 x 6.98 mm

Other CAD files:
hardware/V1.2/3D/BPW34F.step
hardware/V1.2/3D/TLE2072.step
hardware/V1.1/3D/BPW_34_20180209_geometry.STEP
hardware/V1.2/3D/BPX61.FCStd

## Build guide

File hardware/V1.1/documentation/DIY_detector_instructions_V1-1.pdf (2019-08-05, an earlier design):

### DIY Particle Detector

Circuit & board design: Oliver Keller, CERN;
Contact for any questions and further information: oliver.michael.keller@cern.ch

Working Principle:
Ionizing radiation liberates charges in the silicon lattice structure of four low-cost commercial p-i-n diodes, BPW 34 - sold as photo diodes in different variants. The chip’s sensitive layer depth is about 100 µm [2] which makes if a good detector for electrons from beta decays of natural radioactivity. Detection efficiency in such a silicon sensor is about 100 % for up to 100 keV electrons.
Small current peaks induced in the diodes are amplified with a dual stage amplification circuit. The first stage is a transimpedance amplifier configuration applying a factor of 10⁷ followed by a second inverting stage, amplifying the signal again by a factor of 100. The output is AC-coupled and can be directly connected to an oscilloscope or the microphone input of a computer (see notes on schematic about optional R8).
Alpha particles cannot be detected unless the plastic package of the diodes, covering the silicon chip, is removed. The probability detecting gamma or X-ray photons is very low.

Casing Choices:

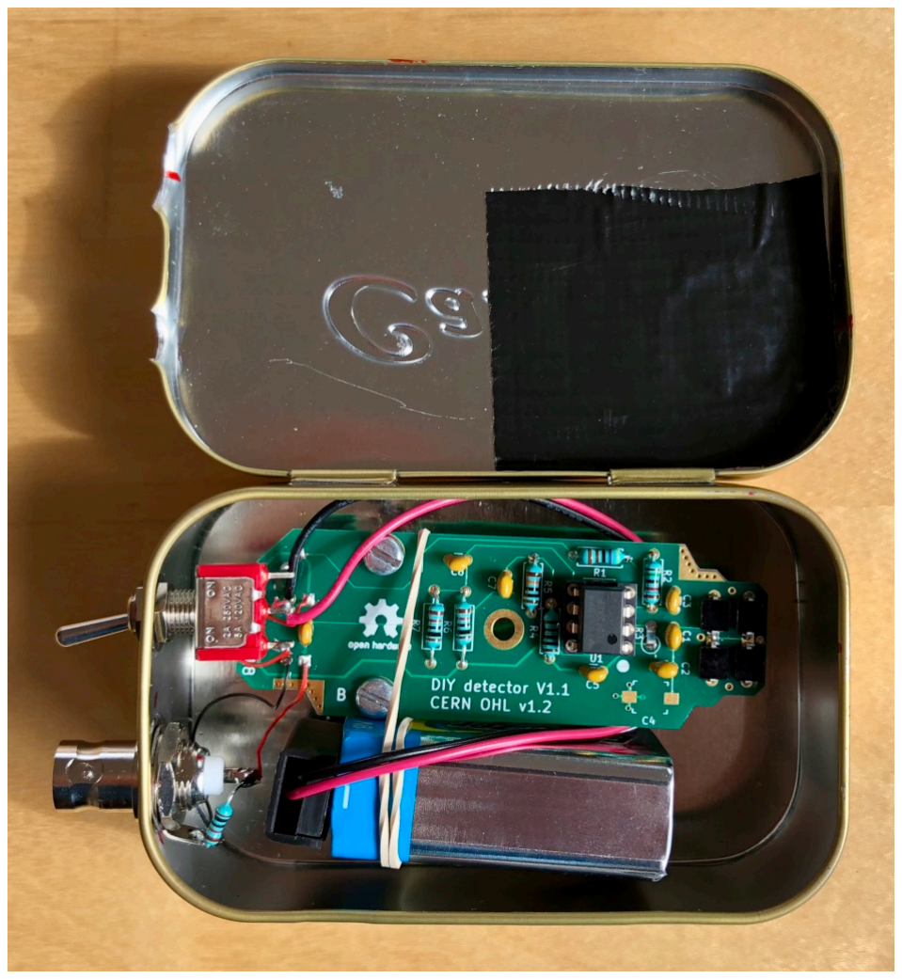
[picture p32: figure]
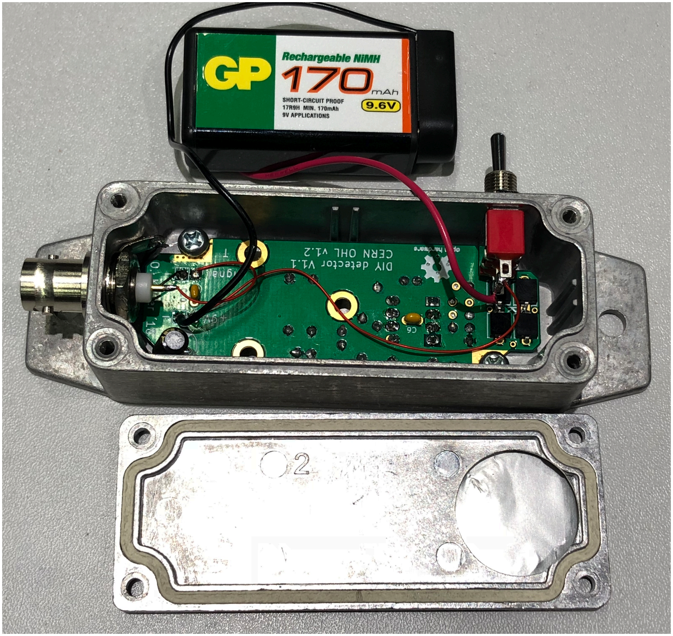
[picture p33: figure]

A metallic case (tin boxes for candies work great, see above) that closes completely and can fit the board together with a 9V battery block. It is important to shield the circuit from any light as good as possible and and block electro-magnetic interferences (hence the metal box as Faraday cage).
A small whole in the case (about 2 cm diameter) in front of the diodes is useful to improve the sensitivity towards particles. However, any light entering from outside must be blocked rigorously with black tape and/or aluminum tape covering the hole.
For professional aluminium die-cast cases (c.f. image on the right) that fit the board precisely please refer to the part numbers stated on the schematic.

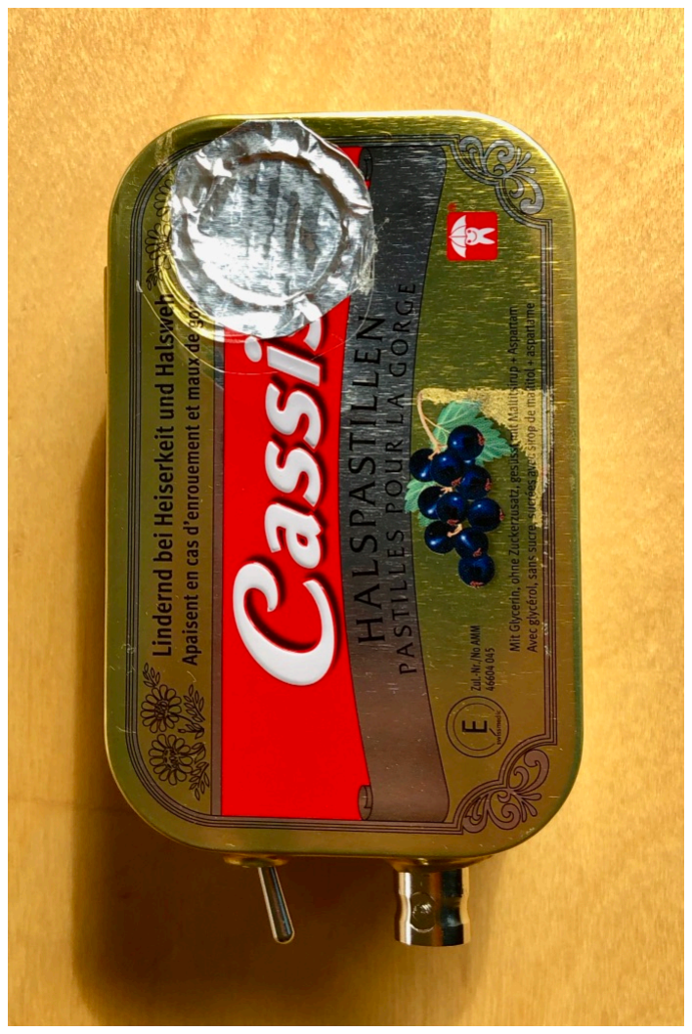
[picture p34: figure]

Build Instructions:
Use the parts overview page as a guide. The assembly should start with soldering the smallest components, all resistors followed by the small yellow capacitors. Their pins should be carefully bend closely to the package to make them fit into the narrow footprints. The image below shows all resistors and yellow capacitors in place. Note how the pins of C6, mounted on the opposite side to U1, are cut very close to the board (right image) in order to provide enough space for U1 which will be placed right above. R3 is bent to the side here but could be also mounted standing upright, depending on available space in the chosen case.

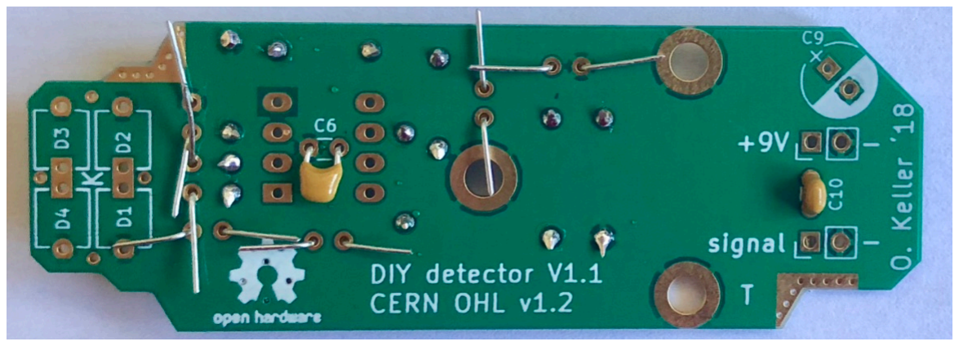
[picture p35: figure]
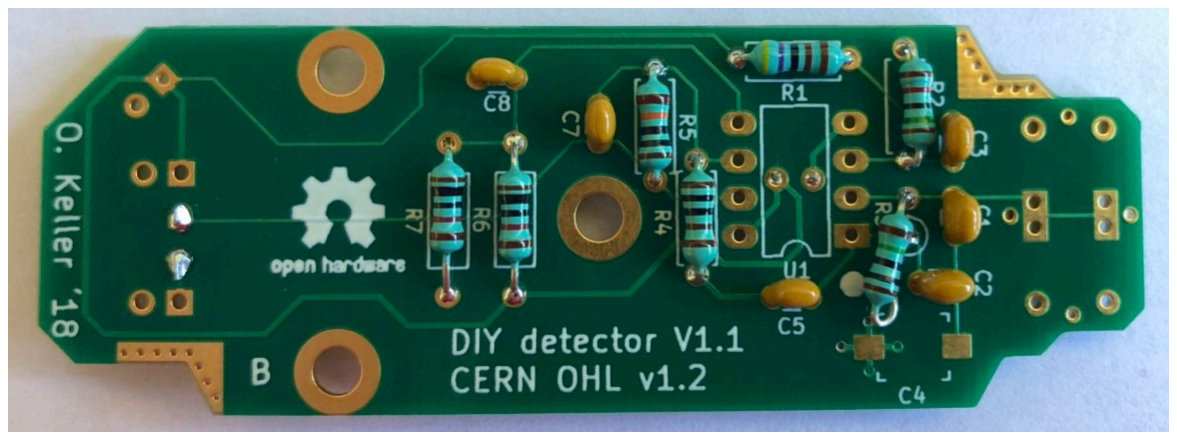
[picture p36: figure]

Top and bottom side with all resistors and small yellow capacitors placed. Bending the pins as show on the left picture keeps the components in place and simplifies soldering. Cut them as short as possible with side-cut pliers afterwards.

When placing U1, D1 – D4 and C9, their polarities must be respected. Pin number one of U1 is marked with a white circle on the board that needs to be aligned with the circle mark on the chip’s package. The diodes D1, D2, D3 and D4 can be mounted on either side, depending on what is more convenient in respect to the available casing. The diodes should be close to the wall of the case, ideally behind a thin ‘window’ covered only by light-tight black tape. The cathode pin of the BPW 34 diode is marked with a little notch (see drawing in parts overview) and must be aligned with the holes for the diodes in the middle of the board (marked with ‘K’ for ‘Kathode’). The large polarized capacitor C9 should be mounted last and can be placed upright or flat on either side of the board as long as its short pin (on the capacitor marked with a white stripe) is aligned with the white half-circle on the board.
The switch should be connected between the red wire of the battery clip and the ‘+9V’ input marking on the board. The board connection marked with ‘signal’ is soldered to the central pin of the wall-mounted BNC socket. The ‘-‘ connection next to the signal output can be used to connect the ground plane of the circuit with the metallic case at the BNC socket. The three big mounting holes in the middle of the board (forming a triangle) are compatible with M3 screws and are as well connected to the ground plane of the board.
After all soldering is finished, the 9 V power rail should be checked for any short circuit. An ohmmeter should show initially about 9 - 10 kOhm when measuring across the two connections of the battery clip.

Using the DIY Detector:
After connecting the battery, close the case and be sure no daylight or artificial light reaches inside. Connect the BNC output to an oscilloscope input, configured to 1 MOhm impedance, DC coupled, timebase 50 -100 us per div, voltage scale 50 - 100 mV per div. Once the power switch of the detector is flipped, the oscilloscope should show a large change of output voltage on the screen.
With a brand new battery (voltage above 9 V) the expected output noise floor is +/- 50 mV around zero. The signal pulses can be triggered at - 80 to - 100 mV (the signal is negative!) using a falling slope edge trigger. Once the battery voltage drops to 8 V and below, the noise floor is typically reduced to +/- 20 mV and the signal pulses can be triggered reliably at around - 35 mV. Since the circuit draws only a few milliampere it will operate for several hours. The upper screenshot one the next page shows a typical signal trace. The area of the signal confined by the pulse shape is proportional to the energy that was deposited by the ionising radiation hitting the sensor (most likely electrons; photoelectric absorption or Compton scattering of energetic gamma or X-ray photons can be observed, but will be very rare).
If an oscilloscope is not at hand, the pulses can be recorded using the audio input of a computer! In this case the optional output resistor R8 must be populated in parallel to the BNC socket. A value of 10 kOhm works well for most multi-functional inputs dedicated to headphones and headset microphones (e.g. most modern laptops). Refer to the schematic for the wiring diagram showing a 4-pin ’TRRS’ compatible jack connection.

Outlook:
The complete design, including experiment descriptions, will be soon published under the CERN Open Hardware License in an education oriented physics journal. The files will appear on www.github.com/ozel. The author is available and will happily respond to any kind of inquires (oliver.michael.keller@cern.ch).

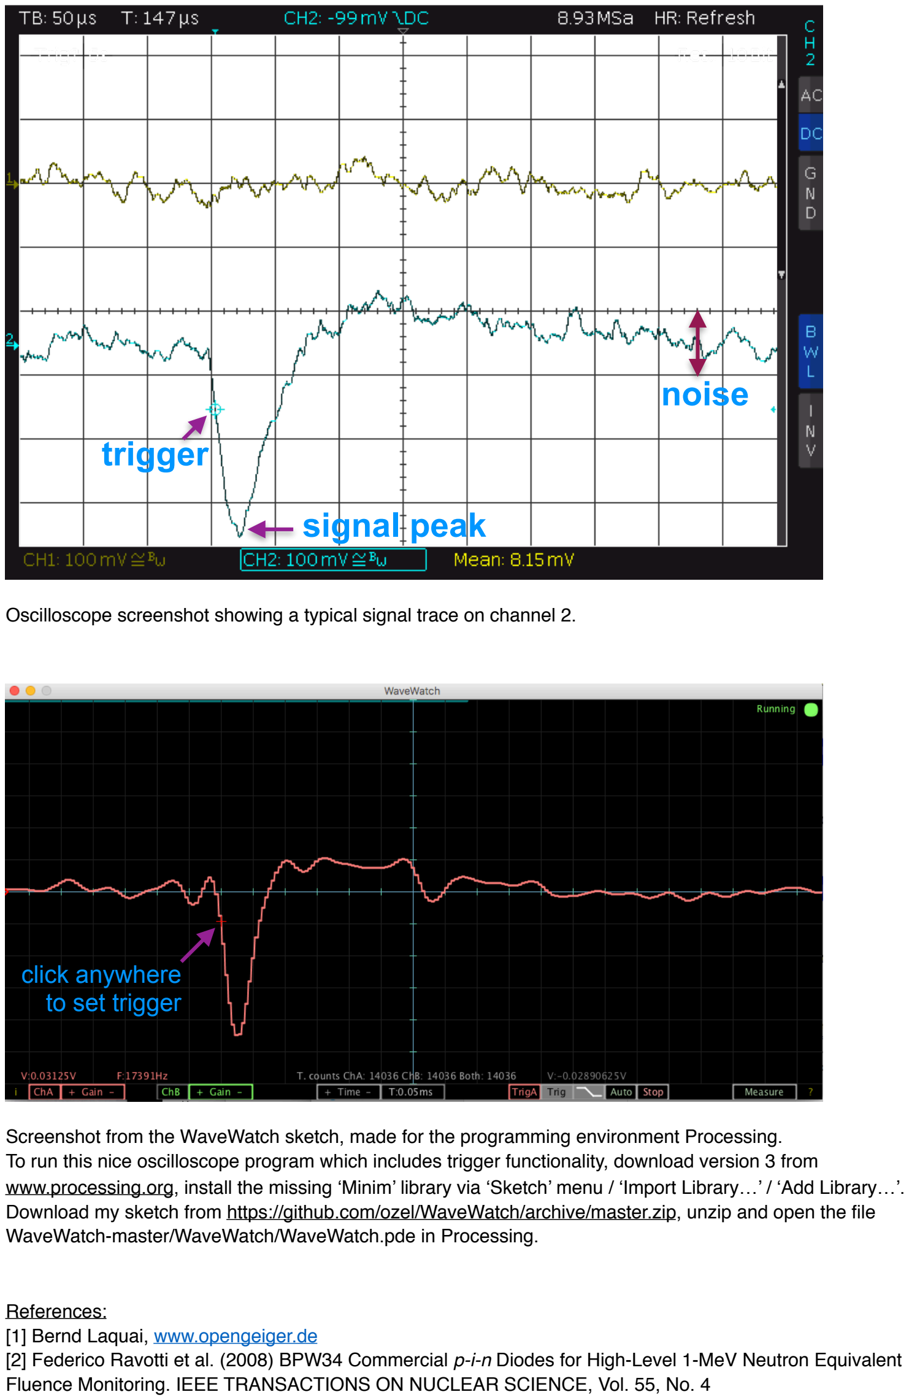
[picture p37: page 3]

Oscilloscope screenshot showing a typical signal trace on channel 2.

Screenshot from the WaveWatch sketch, made for the programming environment Processing.
To run this nice oscilloscope program which includes trigger functionality, download version 3 from www.processing.org, install the missing ‘Minim’ library via ‘Sketch’ menu / ‘Import Library…’ / ‘Add Library…’. Download my sketch from https://github.com/ozel/WaveWatch/archive/master.zip, unzip and open the file WaveWatch-master/WaveWatch/WaveWatch.pde in Processing.

References:
[1] Bernd Laquai, www.opengeiger.de
[2] Federico Ravotti et al. (2008) BPW34 Commercial p-i-n Diodes for High-Level 1-MeV Neutron Equivalent Fluence Monitoring. IEEE TRANSACTIONS ON NUCLEAR SCIENCE, Vol. 55, No. 4

# noise

# signal peak

# trigger

## click anywhere to set trigger

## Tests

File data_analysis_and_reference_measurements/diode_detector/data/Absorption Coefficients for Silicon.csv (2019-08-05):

energyMeV | mu_d | mu-en_d
0.001 | 1570 | 1567
0.0015 | 535.5 | 533.1
1.83890e-3 | 309.2 | 307
1.83890e-3 | 3192 | 3059
0.002 | 2777 | 2669
0.003 | 978.4 | 951.6
0.004 | 452.9 | 442.7
0.005 | 245 | 240
0.006 | 147 | 143.9
0.008 | 64.68 | 63.13
0.01 | 33.89 | 32.89
0.015 | 10.34 | 9.794
0.02 | 4.464 | 4.076
0.03 | 1.436 | 1.164
0.04 | 0.7012 | 0.4782
0.05 | 0.4385 | 0.243
0.06 | 0.3207 | 0.1434
0.08 | 0.2228 | 0.06896
0.1 | 0.1835 | 0.04513
0.15 | 0.1448 | 0.03086
0.2 | 0.1275 | 0.02905
0.3 | 0.1082 | 0.02932
0.4 | 0.09614 | 0.02968
0.5 | 0.08748 | 0.02971
0.6 | 0.08077 | 0.02951
0.8 | 0.07082 | 0.02875
1 | 0.06361 | 0.02778
1.25 | 0.05688 | 0.02652
1.5 | 0.05183 | 0.02535
2 | 0.0448 | 0.02345
3 | 0.03678 | 0.02101
4 | 0.0324 | 0.01963
5 | 0.02967 | 0.01878
6 | 0.02788 | 0.01827
8 | 0.02574 | 0.01773
10 | 0.02462 | 0.01753
15 | 0.02352 | 0.01746
20 | 0.02338 | 0.01757

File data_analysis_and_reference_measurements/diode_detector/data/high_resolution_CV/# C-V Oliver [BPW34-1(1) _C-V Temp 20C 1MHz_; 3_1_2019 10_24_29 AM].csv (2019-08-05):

SetupTitle | C-V Oliver
ApplicationTest | C-V Oliver | Public
TestParameter | Name | Anode | VacStart | VacStop | VacStep | OscLevel | FREQ | IntegTime | HoldTime | DelayTime
TestParameter | Value | CMU1:MF MFCMU | 0 | -5 | -0.1 | 0.05 | 1000000 | MEDIUM | 0 | 0
DutParameter | Name | L | W | Temp
DutParameter | Value | 1E-07 | 0.0001 | 25
MetaData | TestRecord.EntryPoint | true
MetaData | TestRecord.RecordTime | 03/01/2019 10:24:29
MetaData | TestRecord.TestTarget | BPW34-1
MetaData | TestRecord.IterationIndex | 1
MetaData | TestRecord.Preservation | true
MetaData | TestRecord.Flag | #
MetaData | TestRecord.Remarks | C-V Temp 20C 1MHz
MetaData | TestRecord.LinkKey | 884922ad-2af2-4bfe-adb3-650a728b6660
AnalysisSetup | Analysis.Setup.Vector.Graph.Enabled | true
AnalysisSetup | Analysis.Setup.Vector.Graph.ActiveYAxis | 0
AnalysisSetup | Analysis.Setup.Vector.Graph.LeftYAxis | 0
AnalysisSetup | Analysis.Setup.Vector.Graph.RightYAxis | -1
AnalysisSetup | Analysis.Setup.Vector.Graph.XAxis.Name | Vanode
AnalysisSetup | Analysis.Setup.Vector.Graph.XAxis.GroupName
AnalysisSetup | Analysis.Setup.Vector.Graph.XAxis.RunTimeAutoScale | false
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

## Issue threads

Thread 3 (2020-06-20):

ozel/DIY_particle_detector #3: 9V battery does not fit into recommended housing

Matthias32, 2020-06-20:
Please see the image. Or am I doing something wrong?
[image]

ozel, 2020-06-20:
It looks correct in principle, the fit is a bit tight and different 9V battery brands come at varying thickness (I've seen up to 17 mm). Have you tried already to close the lied? There is a bit of space/cut-out within the lid part as well.
Also, C5 should be rather flat like in this picture (labeled C6 in that picture - previous PCB version):
[image]
In case you've soldered C5 already upright, you can still change that by carefully unsoldering the capacitor with tweezers and afterwards bending its legs a bit.

I am using mostly 9.6V NIMH accumulators which are only 15.5 mm thick and come in a black plastic case. That helps with avoiding short circuits - insulation tape around the metal encased battery should help otherwise. In general, the pins of the electronic components must be cut as short as possible to make room for the battery.
Also the case must not necessarily close 100%, it is fine if there is a thin slit, just don't forget to apply the flexible sealing rubber that comes with it in order to have everything light-tight.

It helps if the PCB is thinner than the usual standard 1.6 mm thickness, rather 1 or 0.8 mm. That is of course too late in your case. I'll add another Wiki page about using those tiny die-cast enclosures.
Really consider going with the thinner rechargeable 9V/9.6V NIMH accumulators. It also helps avoiding all the battery waste and they're quite cheap these days!

Matthias32, 2020-06-21:
Thank you a lot for your quick response!

Yes, I tried to close the lid and was not able to do so. I have measured it and you’re right my battery has 17 mm thickness. The depth of the housing till my 1.6 mm PCB is about 16 mm (without seal). So this will barely ever fit.

I will try these 9.6V NIMH, lay down the C5 and cut the component wires a bit more. Maybe I also try to use an 0603 100 nF for C5.

ozel, 2020-06-21:
Yes, using an SMD capacitor for C5 is another good idea, if you have one. And really cut the OpAmp pins short, every fraction of a millimetre counts. ;-) Really do remember to insulate the battery's metal case from all the sharp cut pins... a piece of hard plastic foil cold work, too.

The lid itself has a pocket of a bit more than 2 mm of depth. If you allow for an additional slit between bottom case and lid, you should gain almost those 2 mm of headroom above the bottom case.
Such a slit may look not that nice but is completely fine for operation. The Faraday cage is closed enough as long as the four screws are in place because they establish the main low-conductivity path. Since aluminium always grows a thin non-conductive oxide layer on all surfaces, it doesn't really mater if the bottom case and the lid touch each other on the edges or not for what concerns shielding against potentially disturbing electromagnetic radiation. But you have to make sure it's closed enough to block all light, therefore the white rubber seal should not be omitted and needs to be put in place into the small trench of the lid.

Also, I am routing the connection wires always around the sides touching the curved edges of the battery, such that they're not in the way and adding to the overall thickness.
The on/off switch by the way just fits on top of the diodes, mounted in another hole on the short side of the bottom case. It is then somewhat in the way of the diodes, but that doesn't affect  much the sensitivity in case of the electron-detector variant.
I definitely need to take more pictures of this kind of build, but don't have a readily built on lying around - they're currently all on loan and used by others.

Matthias32, 2020-06-21:
Thank you a lot for the additional recomendations. I will try it out.

By the way: Can you please pass me a link of the 9V battery you are using so I can make sure it is the 15.5 mm one?

ozel, 2020-06-21:
[GP17R8H = 8.4 V version](https://www.gpbmindustry.com/product-page/gp17r8h)
[GP17R9H = 9.6 V version](https://ind.gpbatteries.com/pub/media/uploads/pdf/rechargeable_NiMH/by_series/standard_series_cylindrical/GP17R9H.pdf)

I prefer the latter for its higher voltage and did the alpha energy calibrations with that one. Since you're building the electron variant anyway, it doesn't mater at all.
Both seem to come in the same black plastic case.

ozel, 2020-06-21:
Thanks, @Matthias32 for reminding me about missing info related to the small aluminum diecast enclosures.
I've added two new wiki pages [Enclosures](https://github.com/ozel/DIY_particle_detector/wiki/Enclosures) and [Batteries](https://github.com/ozel/DIY_particle_detector/wiki/Batteries) so I'll close this now. Feel free to open the issue again or create a new one if you have more questions.
 
And please post a picture of your finished detector online so I can update the [Gallery](https://github.com/ozel/DIY_particle_detector/wiki/Gallery)! :D

closed 2020-06-21 by ozel

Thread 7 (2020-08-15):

ozel/DIY_particle_detector #7: Mounting the PCB

SteveF161, 2020-08-15:
Apologies for a noob question. My son and I have been building the electron detector as a lockdown project. We are ready to mount into a nice metal tin but we are not sure of best way to do so. I'm thinking some sort of motherboard/PCB stand-off but I'm not sure what size these need to be. Are the PCB holes for M2 , M2.5 or M3 stand-offs? Is metal better than plastic? Seems you only buy standoffs in quantities of 100+ so I'm trying to avoid expensive trial and error!

(Incidentally, the board proved really easy to build for a couple of inexperienced people. I haven't soldered anything other than audio cables for many years. My son has done only 3 or 4 joints in school. We both suffer from hypermobility of the finger, which doesn't help.  So, we checked every joint and all looks good so far. We plan to build the alpha detector next if this works OK.)

Matthias32, 2020-08-15:
I would recommend M3 metal. It should be possible to order less than 100 pcs. Just check on Amazon there are also some collections like this one:

[https://www.amazon.de/AMZANDY-NEW-Abstandshalter-Abstandsbolzen-Motherboard-120/dp/B0825XY6VD/ref=sr_1_1_sspa?__mk_de_DE=%C3%85M%C3%85%C5%BD%C3%95%C3%91&dchild=1&keywords=m3+abstandsbolzen&qid=1597494331&sr=8-1-spons&psc=1&spLa=ZW5jcnlwdGVkUXVhbGlmaWVyPUEyVEw3UkU2SFRYSDlFJmVuY3J5cHRlZElkPUEwMTU3ODI0MlNEOTVBWE9QUko2SiZlbmNyeXB0ZWRBZElkPUEwOTIyODg2MUZJMERMN0dNUjRaNiZ3aWRnZXROYW1lPXNwX2F0ZiZhY3Rpb249Y2xpY2tSZWRpcmVjdCZkb05vdExvZ0NsaWNrPXRydWU=](url)

Depends on from where you want to order. I was checking the german Amazon page for example.

SteveF161, 2020-08-15:
Many thanks for a swift response. That particular one isn't available on UK Amazon but I found some similar ones. and not too expensive.

ozel, 2020-08-19:
Hey @SteveF161, thanks for your feedback! Motherboard stand-off screws (or 'distance bolts' ?) could work but at least older ones often use non-metric threading. I use M3 parts made from metal since the holes and board edges are connected to the circuit ground. Using metal parts can improve the noise to signal performance - depending on the case. And using one of the holes should be enough.

I heard RS online ships for free in the UK also to private persons, their "M3 PCB spacer" should be a good choice:
https://uk.rs-online.com/web/p/standoffs/1613631/
(plus one M3 screw and a nut per detector)

Please do not hesitate to post pictures of both board sides if something doesn't work, it is rather easy to spot soldering problems visually in this design. And definitely consider posting some pictures of the finished detector [here](https://github.com/ozel/DIY_particle_detector/issues/4) so I can add them to the wiki Gallery. :-)

I'll keep this issue open in case others have more mounting related questions. So far this is covered here in the wiki:
https://github.com/ozel/DIY_particle_detector/wiki/Assembly-Instructions

closed 2020-12-09 by ozel

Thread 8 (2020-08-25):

ozel/DIY_particle_detector #8: Debugging the electron detector

SteveF161, 2020-08-25:
Another noob question: Is there a guide [...idiot level, of course...] to debugging construction problems? I have a board that's built and where every joint and connection appears to be correct, and where all have been continuity tested with a multi-meter to different parts of the PCB (i.e. not just checking across the component but from wherever the component connects to next). The detector shows a nice pulse when switched on and off in the web oscilloscope, but gets no pulses from ~ 10g of KCl. Is there a recommended set of steps for tracking down problems? Does the web oscilloscope software need any specific adjustment?

Steve

ozel, 2020-08-25:
Hi Steve, 

there is a troubleshooting list in the wiki:
https://github.com/ozel/DIY_particle_detector/wiki/Assembly-Instructions#troubleshooting

Seeing a signal when switching the battery is already very good!

If it is really just 10 grams, it should be right on top of the diodes inside a small plastic bag. If you have more, like a full 100g salt dispenser wrapped in its original paper/carton you could put it as well outside, on top of the detector case (unless the diodes are then very far away inside the case, like further than one or two centimeters from the outside).
10 grams of KCl will result only in about 1.3 pulses per minute per covered diode. You've built the electron detector with four diodes, right? In this case, you should observe about 5 pulses per minute maximum, it may still require some patients to wait for them. :-)

With my web oscilloscope (https://ozel.github.io/DIY_particle_detector/data_recording_software/webGui/) one usually has to adjust the red line trigger level and put it much closer to or further away from the noise level in order to capture pulses (signal range depends a lot on the smartphone/laptop hardware). Use the two up/down arrow buttons to adjust the red line threshold level.
You could also have inverted signals (i.e. detector pulses going up than downwards) in this case you have to move the red trigger line above the noise levels. You can fix that by swapping the ground and signal connection on the 3-pin or 4-pin jack connector. 
Btw, double-check that you have soldered those connections correctly as explained here:
https://github.com/ozel/DIY_particle_detector/wiki/Cables#connection-with-a-headset-socket

If you still see no pulses, it could be too much light reaching inside the case and onto the diodes. Throw a black pullover/shirt on top of the detector case and try using it in a dimmer room. If this helps, you just have to find and patch some tiny slits and holes of the case with black tape.
The last resort would be to measure your output signals with a real oscilloscope and compare the noise voltage levels with the screenshots of mine (in the main readme). But usually, problems can be identified without that.

Don't hesitate to post pictures of both board sides and your headset connector wiring. The latter is always a kind of paint point to get right.

SteveF161, 2020-08-27:
A brief update before I spend a few days off-line: I upped the amount of KCl to about 25g and put it on top of a stand to raise it closer to the detector diodes. However, I stopped seeing the on/off pulses when the detector was switched on and off. I checked and rechecked everything but couldn't find an obvious fault. Today, I was tinkering with Windows 10 microphone settings and took the blindingly obvious [...to other people...] step of monitoring the microphone socket of the detector via the headphones. Now, suddenly, I'm hearing white noise and soft clicks every 10-15 seconds when the detector is switched on! The web oscilloscope (DIY pulse detector) started showing the white noise but very few clicks. (These seem to be only a little above the noise level, and the pulse detector only seems to detect even the white noise about 10% of the time.) My thoughts now are that this is partly a software problem, which I might tackle by rebuilding an old laptop under Ubuntu, or that there's stray light causing excess noise and I can fix that with some black tape upon my return.

ozel, 2020-08-27:
Check that the battery has still enough power! If the voltage drops below 8V (measured across the disconnected battery), it is rather empty. It might deliver enough current for a few seconds if you give it some rest, but it will turn into an unreliable power source if it is drained too much.
If the detector was on for about 2 days, it's probably drained. I recommend buying cheap 9V accumulators & chargers: https://github.com/ozel/DIY_particle_detector/wiki/Batteries

The many microphone input settings of headset sockets can be a tricky problem to get right. On Mac/iPhone/iPad the headset connector switches only to "external microphone" mode if the detector is already powered ***before*** plugging it! And there is no way to do the switch manually, it is detected only automatically on Apple hardware. It also works with the lightning-to-headset adapter, by the way (if the detector is powered before plugging it in).

There could be some similar automatic detection going on with certain Windows machines, depending on the hardware.
Another problem is that some PC headset inputs are really flexible and can also function as a regular stereo or mono microphone input. A 3-pin connector and different wiring would be needed, if the socket is in that microphone mode, see: https://github.com/ozel/DIY_particle_detector/wiki/Cables#audio-jack-connector-overview-35-mm-trstrrs) 

If you want to be 100% sure that the correct headset mode is recognized and selected within the web oscilloscope, please plug a regular headset and whistle/hum into the microphone. You can also experiment with the red trigger level line ob the web scope app that way and see how the triggering work works (frozen image everytime the signal goes below the line).
You did not mention if you adjusted the trigger level in the web oscilloscope app. The red line needs to move as you push the up/down on-screen buttons. It should be as close as possible *below* the noise levels, but not too close to them.
Unless your pulses got upwards because of twisted signal and ground wiring. In that case, the trigger line would need to be close *above* the noise levels.

In principle, it is possible to hear the pulses as very short glitches, depending on audio settings. But I would not check for them that way before you have seen them on an oscilloscope plot.
As described in the troubleshooting list, try snipping your detector case hard & briefly with a finger. If you can't excite short sine-like waves that way, something is still wrong on the soldering side.
My main guess right now is that your trouble is related to setting the trigger level correctly (in the app, not inside windows).

Also consider testing it on a smartphone or tablet with Firefox or Chrome (Safari on iOS). If the OS is recent enough, it should be able to access the headset socket's microphone input. Remember to always power the detector on before plugging it in. If you switch it off to check for that power-off pulse, please unplug and re-power before plugging it in again. A browser reload would be also good after replugging it.

If all of this doesn't get you anywhere, consider trying another microphone/audio input. Like the cheap CM108 USB soundcards. They are 1-2$ on Aliexpress, and a bit more on Ebay: https://github.com/ozel/DIY_particle_detector/wiki/Soundcards
You'll just need to make another 3-pin TRS jack cable for those instead of the 4-pin TRRS one for headset sockets.

SteveF161, 2020-09-01:
After spending a day or two visiting family, I rebuilt an old laptop (Asus Eeepc 901, vintage 2010, Intel Atom processor, 2GB RAM, 32GB SSD) to run Lubuntu and connected the detector to its mic input, As expected, there is a lot of electronic noise but I do see the up/down pulses from the detector and you can fairly easily distinguish them from the false pulses caused by noise peaks. Conclusion: it's working! Thanks for help and suggestions. My son and I will probably blog this later, complete with construction photos and screenshots.

ozel, 2020-09-01:
awesome! please post the blog link once done :-)
The noise is expected as the circuit got only a few thousands of charges to work with for each particle. An external USB soundcard might improve it, but usually not by much. It can be worth trying different gain settings, I've had the best results at maximum gain but anything that looks like noise-canceling disabled (see the wiki page on Soundcards).

SteveF161, 2020-09-01:
I've blogged it here: https://clanhouse.com/cern-at-home-building-a-particle-detector

closed 2020-09-01 by SteveF161

ozel, 2020-09-01:
Since you're using the website scope that shows the signals rather zoomed out (optimized for alpha pulses): 
you may have a better experience with the WaveWatch processing sketch, as it allows zooming into the pulses. Copied from the main readme (as I need to put this more prominently):
To run this program written in Processing, download Version 3 from www.processing.org and install the missing ‘Minim’ library via the ‘Sketch’ menu / ‘Import Library...’ / ‘Add Library...’. 
Download my version of the WaveWatch Processing sketch from https://github.com/ozel/WaveWatch/archive/master.zip, unzip and open the file WaveWatch-master/WaveWatch/WaveWatch.pde in Processing.

If you want to explore some "learning to program" aspects with your son (for which Processing is perfect...), I've uploaded a very simplified oscilloscope sketch here: [simple_audio_scope_for_Processing.zip](https://github.com/ozel/DIY_particle_detector/files/5157902/simple_audio_scope_for_Processing.zip)

It allows setting a trigger level and count particles. Some summer students developed this with me a while back. It could be relatively easily extended to calculate a count rate per minute or per 10 minutes etc.
The WaveWatch sketch got better trigger and zooming functionality, of course. But it's more complicated to understand and work with its code directly for making extensions.
Processing is multi-platform, by the way. Should work well on Lubuntu. Only the selection of the sound device can be annoying. :-)

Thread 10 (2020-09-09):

ozel/DIY_particle_detector #10: Format of Example Data

SteveF161, 2020-09-09:
I'm trying to open one of the reference data sets (the one from the 9.44g of KCl) and I'm getting a pickle error:
`    df = pd.read_pickle("./data/KCL_9-44g_1x3x3cm_touchingdiodecase_pulses_2019-07-08_23-07-18___947___11-47.pkl")

  File "/home/steve/.local/lib/python3.6/site-packages/pandas/io/pickle.py", line 182, in read_pickle
    return pickle.load(f)

UnpicklingError: invalid load key, 'v'.

`
Can you confirm what format the data is in and what versions of pandas/pickle/python were used?

(Background: The data analysis python script isn't finding any pulses in the data files that I record with the JavaScript pulse detector. I've looked at the data in my files and I see a lot of values around -32000, which is the sort of thing I'd expect to see from some kind of 15 bit signed/16 bit unsigned conversion problem. I was trying to compare against a reference data set to test the hypothesis.)

ozel, 2020-09-09:
Have you checked out the files using git LFS as explained in this section: https://github.com/ozel/DIY_particle_detector#reference-measurements-and-plots?
Since large binary files should generally rather not be stored in plain git, I put them there. 
Alternatively, you can download the files from the Zenodo archive link as a whole or from the Github website one by one: https://github.com/ozel/DIY_particle_detector/tree/master/data_analysis_and_reference_measurements/diode_detector/data

I will come back regarding minimum module versions, but Python 3.6 should be good in principle.

Please note: since you are not using the same USB soundcard like me, one of the 1-2 $ low-cost CM108 USB dongles described in [Soundcards](https://github.com/ozel/DIY_particle_detector/wiki/Soundcards), you will certainly have different pulse amplitudes maybe even saturation depending on the gain settings. 
In order to adjust your microphone input gain in the system setting for a useful range, I would suggest to either use the WaveWatch Processing sketch or `pulse_recorder.py`, both described more detailed in the new Wiki page [Software](https://github.com/ozel/DIY_particle_detector/wiki/Software). 
The latter python script requires the pyqtgraph module and in turn Qt, but those large dependencies can be well handled if you install your whole python environment via `anaconda` (very very much recommended).
You'll need to adjust the input gain settings such, that -300 is a threshold level where the noise is well below that (like +/-200 on average).

SteveF161, 2020-09-09:
D'Oh! If I'd looked, I'd have seen that the one I had downloaded was only 133 bytes! The full 7.6MB file works correctly and I can see the data in it is very different to mine.

My data does look suspect but the fact that the JavaScript detector sees around 500 pulses over 3 hours makes me think that sound card is working OK and the problem might be data conversion. 

The laptop that I'm using is running Lubuntu on an early model Intel Atom processor. I've not yet found a Python Qt library that installs on it. I may well spend a few pounds on the cheap soundcard and link it to my Raspberry Pi 4 on the grounds that (a) I'm pretty sure I can get a working Qt for it and (b) it's probably a more capable machine than the antiquated laptop.

ozel, 2020-09-09:
Did you try installing pyqtgraph with Anaconda?

As I wrote before, please have a look at the WaveWatch program: https://github.com/ozel/DIY_particle_detector/wiki/Software#processing-based-audio-oscilloscope
Processing is based on Java and should run flawlessly on your old Intel Atom system. It allows you to zoom in on the x-axis such that you can actually check for the correct pulse shape (see the screenshot, that I just uploaded on that wiki page). At the moment, it doesn't show the raw value of the trigger level due to its fancy voltage calibration feature but I can fix that quickly in the next couple of days if it helps you.

SteveF161, 2020-09-11:
Update: I bought the cheap sound card on Amazon (£7.99 : Sabrent AU-MMSA). I fitted to the laptop and I get a much cleaner signal. the noise level is far lower and the electron pulses stand out perfectly. However, the data that I save is still unreadable in the analysis script which continues to recognise zero pulses.

Next, I moved the sound card to my raspberry pi4. As expected, the pi4 definitely has more oomph than my antiquated laptop. Again I had a clean signal with very obvious peaks but the saved data files are still unreadable in the analysis script.

I downloaded the python data recording script (...and the interminable dependencies...) to the pi4. It works very well, though the noise level _appears_ much higher as it is scaled differently. Most importantly, the saved data files **work** in the analysis script. It might be worth taking a look at the JS script to see if there is anything odd or if this is just expected but unreasonable behaviour of different sound cards

I'm in the middle of tinkering with the sensitivity levels to cut out false pulses. I'm currently seeing around 0.9CPS which is about 30-50 times higher than with the other app and the energy spectrum looks nothing like I'd expect for beta. Clearly, tuning is required.

ozel, 2020-09-11:
Good to hear that works now for you!
This scale difference in the oscilloscope view is what I meant. The WaveWatch Processing sketch did not work for you on the EeePC?
If I find some time, I will try to give the web browser oscilloscope a little bit more love and functionality, but it is really rather painful to develop. That said, we can consider the situation already quite lucky since it still works after one year which means the javascript WebAudio API seems to have stabilized after all...

In principle, the generated .msgp files should be loadable in the analyser python script. Could you attach one of your files that did not work in the next comment? Just zip it and drop it on the comment field.

Since you've built the electron-detector version so far, looking at the energy spectrum will not provide a lot of interesting information in general. See the Wiki entry on [Energy Spectra](https://github.com/ozel/DIY_particle_detector/wiki/Energy-Spectra#electron-energies).

In general, the recording of waveforms and corresponding `analyse_and_plot_pulses.py` script is really meant for being used in combination with **the alpha-spectrometer variant only**. Due to a few different component values,  much longer pulses are produced in both cases, alphas and electrons! I haven't used the analyse script myself with electron-detector data and it is very likely that it does not yield useful results because important pulse characteristics are different (steepness of pulse slopes and width of pulses).
The other aspect is as discussed the threshold level (THL variable), which is by default at -300 in both scripts, the reorder and analyse python scripts and is only valid for the **alpha-spectrometer variant**. The electron-detector variant got quite some higher noise value, larger than -1000 is typical if I remember well.

You may have seen the electron energy spectrum in [my paper, figure 7](https://www.mdpi.com/1424-8220/19/19/4264/htm).
That however was as well recorded with the alpha-spectrometer variant of the detector, and not with the electron-detector version that you built so far. Conversion from one to the other is doable, by the way. Even unsoldering of the diodes works with tweezers/small pliers and if one pulls while a third-hand navigates the soldering iron.
But if you have spare PCBs, using those would be better of course.

SteveF161, 2020-09-11:
There's a non-working file [attached.]
[DIY_Particle_Detector_2363-pulses_2020-09-02_14-42.zip](https://github.com/ozel/DIY_particle_detector/files/5210324/DIY_Particle_Detector_2363-pulses_2020-09-02_14-42.zip)

I'm working with THL around -2500 on the electron detector but I'm not yet sure if this is still too small. The average noise level looks to be about -1000 but there are quite a few higher peaks which I think may be EM noise from vehicles on the busy road outside my house.

My sense-check on the data is to look at the energy spectra which I'd (naively) expect to be convex rather than concave near the origin. The fact that I'm seeing concave makes me suspicious of the settings. 

Anyway, I have a long collection run ongoing at the moment and I'll see what that contains.

ozel, 2020-09-11:
thanks for the file! 
You could as well post screenshots from good pulses and suspected noise hits. Otherwise, it is really difficult to help.
EM noise can be an issue (e.g. a running laundry machine or old fridge close by) or just a little bit of light leaking inside the case will as well increase the noise but in a very subtle way (while too much light just saturates everything). You can be suspicious once you see regular 50/60 or 100/120 Hz noise... one segment on the x-axis is 1/48000 seconds wide, so you can roughly estimate the frequencies.

The pulses that trigger really need to have that distinctive, asymmetric and bipolar **shape** as in the pictures, e.g. https://github.com/ozel/DIY_particle_detector/wiki/Software#processing-based-audio-oscilloscope
If the pulses do not look like that, you can really skip further recording or have to increase/lower the threshold until only good ones trip the trigger. The analyse script does not magically find something *within the noise* beyond us humans, that is for sure. ;-)

SteveF161, 2020-09-11:
I've attached a couple of the "good pulse" screenshots, one from each capture method. I can't post shots of the "bad" pulses as they only seem to be a problem on the python script collector and they don't actually show up on the display. It may be that the display is not refreshing as often as it should. I can send a data file when the collection run is finished.

[drive-download-20200911T164921Z-001.zip](https://github.com/ozel/DIY_particle_detector/files/5210547/drive-download-20200911T164921Z-001.zip)

ozel, 2020-09-11:
those pulses look perfect, note that you can also zoom into them in the pyqtgraph window by changing the window config settings, via right-click or the gear symbol. Or just pull the window very wide.

the only additional info that the analyse script can provide in your case with an electron-detector is finding **additional pulses** within the recorded waveform snippets (4096 values each). But with a low-intensity source like KCl you should not really see more than one pulse in 4096 value snippet on average.

Have you adapted the threshold value THL in the analyse script? It has to be the same one as the one used in the recorder. Running the analyse script on your data with the original THL of - 300 is expected to do a lot of things wrong as it is intended for the alpha-spectrometer variant only. And as I wrote before, there are further reasons why it will not properly find electron-detector pulses anyway.

SteveF161, 2020-09-12:
Thanks for the response. I'm guessing that the calibration of the electron detector is quite different to that of the alpha detector. I'm seeing an energy spectrum of vaguely the right shape but the energy looks completely wrong. I'd expect the maximum around 0.65MeV and nothing above ~1.36MeV except for the single gamma peak at 1.4 MeV. (I'm not seeing the gamma peak but I remember reading that the detector has low efficiency for gamma, so I'm not worrying about this at present.)

I had to tinker with the script to get all the pulses to display but I don't think I've changed anything significant. I've mainly adjusted THL and re-included it in the peak pulse calculation as it is quite significant compared to the sizes of many pulses. 

I may try to hack a bit further to get better pulse detection for electrons (...which will require me to do some background study in pulse detection first!...) and to calibrate against known properties of KCl spectrum.

I've attached some of the spectra.
[K40 with electron detector - sample graphs.zip](https://github.com/ozel/DIY_particle_detector/files/5212478/K40.with.electron.detector.-.sample.graphs.zip)

ozel, 2020-09-15:
The *shape* of one of your spectras looks actually quite ok, ignoring the x-axis labels of course. 
But it depends on your modifications of the code if it is a real one. The important parameters for tweaking are:
```
min_g = -20 # steepeness of falling edge slope, almost vertical
min_length = 44  # about 0.9 ms at 48 khz sample rate
max_length = 120 # about 2.5 ms, tolerates some alpha-pileup
```
With these default settings for the alpha-spectrometer. The electron-detector has much shorter pulses (25 - 100 us max.) as you can see here: [image]
The length values are in numbers of samples, so those depend on the sample rate. 
If your spectra where recorded with those same min/max length setttings, they could not come from the real pulses. They would need to be set much shorter. Also min_g may need to be adapted. The extra options like SHOW_DETECTED_PULSES are there to help with debugging trigger parameters. If the pusles are not all well aligned such that there is no clear "valley", the paramters do not fit to the pulse shape. C.f. the green "overlayed pulses" figure 7a in the paper.

Rergarding energy calibartion and the possibility to observe characteristic gamma/x-ray peaks with the electron-detector:
The recorded electron "spectrum" is basically a convolution of the diode geometry, amplifier/threshold noise, compton scattering of gamma particles (see below) and contious beta decay energy spectra (if emitted from the source nuclide, but mostly both kinds are emitted as with e.g. potassium-40 in KCl).

**The main aspects between the detector signals of both different detector varaints are those two things**: The different pulse geometry described above and a different lower energy threshold. It should be higher than the 33 keV of the alpha-spectrometer due to the 4 diodes (increased capacitance, reducing SNR) and different amplification factor/filtering of the circuit. I would guess something between two and three times as much: 66 keV - 100 keV.
Above 100 keV, compoton scattering of gamma photons (=incoherent scattering) completley dominates in silicon sensors as you can see in this diagram attached:  (generated from https://physics.nist.gov/PhysRefData/Xcom/html/xcom1.html).

[image]
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

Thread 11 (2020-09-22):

ozel/DIY_particle_detector #11: Alpha particle pulses

Matthias32, 2020-09-22:
Dear Oliver,
my beta detector works well but I'm not sure about my alpha version. Besides some small pulses (beta i guess) there are also some lager ones which goes also a lot in the positive voltage area. I also see often these "double pulses". Is this normal for the alpha sensor variant?
[image]
[image]

_Originally posted by @Matthias32 in https://github.com/ozel/DIY_particle_detector/issues/10#issuecomment-696834811_

ozel, 2020-09-23:
The second image looks quite good. 1-2 ms pulse width as expected on the downward-facing part.
The full amplitude is not shown, but if it is larger than -8 mV it should be a nice alpha particle pulse. Judged only by the large overshoot on the top, it probably is one. This amplitude threshold level of -8 mV between electrons and alphas (see main Readme file) is valid for short BNC cables,  1 megaOhm input resistance and a 1:1 attenuation setting at the oscilloscope channel.

The regular artifact in the first image looks like EM noise or stray light - it seems to be close to 50 Hz. Could you post a picture of your whole measurement setup and also show the alpha radiation window if you made one?

Matthias32, 2020-09-23:
This was the setup. The alpa radiation windows is just a hole in the bottom of the case.
[image]

ozel, 2020-09-25:
From this picture, it is difficult to give advice. I would need to see how the case itself looks like, including the radiation window etc. 
Did you cover the diode at least with foil like described here: https://github.com/ozel/DIY_particle_detector/wiki/Diodes#pin-diodes?
Even with that foil, it may still need to be used in only dark environments or with a piece of black cloth covering the detector plus specimen. Did you try black cloth instead of the aluminum foil?

Honestly, the aluminum foil will do not much. It is usually not even good in blocking light due to tiny cracks or small openings/folds close to the table surface. And for shielding low-frequency EM radiation - ***which is absolutely required here*** - it also does not work since aluminum always builds up a non-conductive oxide layer. It simply cannot be used to form a proper Faraday cage.
It may shield some high-frequency (GHz) EM radiation but that is usually not a problem with the DIY particle detectors and their low-pass characteristic.

Matthias32, 2020-09-30:
Thank you a lot. This is the detector below the aluminium foil. 
[image]
I will try to block the light with a black towell instead of aluminium foil.

ozel, 2020-10-05:
Hi Matthias,
that looks great in principle. But you either have to cover the diode itself or the hole with a thin metal foil (e.g. from an old foil capacitor) as shown in the first picture here https://github.com/ozel/DIY_particle_detector/wiki/Diodes#pin-diodes
or, alternatively, put a thick black piece of cloth on top of all: detector and specimen.

Even with a metal foil glued on top, the diode should be always facing down and away from sources of light.
Too much light saturates the amplifier completely and procues a flat line on the output. 
The tricky condition is with just a little bit of stray light, that keeps the detector running in principle but also raises the noise floor quite a bit. 
One irritating aspect in your oscilloscope picture above is the fact that the left side is flat and the noise waveform starts mid-way only after the trigger. Usually, electromagnetic noise or too much stray light would produce continuous waveforms.
So maybe, in addition, one of the capacitors close to the first amplifier stage is missing or has the wrong value?
Or could the diode be picking up some additional light from the oscilloscope in the moment of the trigger?

Keep me posted.

Matthias32, 2020-10-08:
Hi Oliver,
no the battery is inside the case. For the measurement I put the case with the uranium glass below the aluminum foil. The short cable was used for another setup using a little portable scope. But the big scope in the picture has a better resolution for sure. 

Where I can get these thin metal foils from? Or how should I disassemble the foil capacitors to get the foil?

ozel, 2020-10-09:
> Where I can get these thin metal foils from? Or how should I disassemble the foil capacitors to get the foil?

Many types of foil or [film capacitors](https://en.wikipedia.org/wiki/Film_capacitor) should work as long as there is no electrolytic liquid chemistry inside - non-polar film capacitors should be mostly dry inside. I used those old types from an old electronic device (pre 1980 I would say) which seems to have a kind of "ceramic" layer or paint around them. I simply cut it open with strong pliers. If I find the pictures again, I'll post one. 

Did you have some luck with thick black cloth on top of everything? That should really work as long as there is not even the smallest gap between the table surface and cloth allowing light leaking inside.

Matthias32, 2020-10-10:
Dear Oliver,
I have tried to disassemble some capacitors and it went very well. Thank you a lot! But I still have some strange issues. Let me try to explain (which is not easy for me):

1. If I use the thin foil I get a nice low noise signal which looks good. I’m able to get some beta particles but no alpha particles. I guess it is because the foil is still too thick for alpha particles?
[image]
[image]

2. If I put some cloth on the assembly with no additional radiation window (no foil) I see a lot 50 Hz noise. Now if I touch the housing with my hand the noise gets suppressed.
[image]

3. If use just a thick black tape on the radiation window I have a clear low noise signal. If I put anything on it (my hand, probe, foam, any other material) the 50 Hz noise is again there. While touching the metal housing the noise disappears. 
[image]
[image]

Looks like some ground or capacitive issue? What do you think?

Somehow the previous aluminum foils setup suppressed most of the now occurring 50 Hz noise. By the way I have turned off nearly all lights in my cellar workshop, only using an LED tube.

So is this noise caused by EMV or a 50 Hz driven light source? I have no idea…

ozel, 2020-10-14:
Hi Matthias,

thanks for your many pictures and explanations, it makes it much easier to follow!
This is a very interesting situation I had not observed so far. I am guessing that you have/had a combination of light and "tethered" EM noise issue. The waveform shape from an incandescent light bulb would look exactly the same like EM coupling from the mains supply as both use the same 50Hz frequency. But the observed amplitudes of both effects should be different of course.

I guess what you observe in 2) and probably as well 3) is leakage current coming from the main power (you'd short circuit the tiny leakage current on your mains' earth connection by touching the case). The ground/shield connection of all BNC sockets on mains-powered oscilloscopes is usually directly connected to the earth of the wall outlet (via the so called "Schuko" in Germany). If your type of wall socket allows that, you could try turning the oscilloscope power connector by 180 degrees and with some luck the leakage current could drop depending on the internals of the power supply inside the oscilloscope. But the source of leakage current on the earth connection could be as well some other high-power device on the same mains network like a fridge or kitchen stove in other rooms (up to 2 mA of AC voltage are allowed to be disposed by a power-hungry device on earth connections and per device if I remember correctly).
So the perfect way to test this theory is using either some USB powered oscilloscope & computer (without mains power) or just the headset input/soundcard of a laptop or smartphone. Or even better, in one of your gallery pictures you had a battery-powered portable oscilloscope - that would be best!

Now the question is: how does the leakage current couple into the detector circuit? 
Is it possible that the metal case of the diode is touching your aluminium case? Maybe just barely - the thin oxide layer on aluminium could play a role here. If both are in good low-resistance contact the circuit should not work because the diode case is the sensitive cathode and must not be grounded accidentally via the grounded metal case. But if diode and aluminium case are close together - almost touching or separated only by a thin layer of aluminium oxide - the leakage current could couple capacitively into the amplifier via the diode case, as you suggested.

I had assembled an alpha detector similar to your approach about a year ago. Unfortunately I gave it away, so I can't confirm, but I think that I had isolated the diode with some tape and then pressed it into the hole of the aluminium case. The purpose of the tape would be that aluminium case and diode are electrically well separated. The type of tape could even play a role with different permeability and electrostatic properties... could be worth trying out few different ones if the first one doesn't work right away.

What is your alpha source by the way? It is shielded/encapsulated well, the emitted alphas could loose already most of their energy before they reach the detector, irrespectively of the additional capacitor foil.
What is the amplitude of your largest pulses in 1:1 input attenuation config and at 1 Mega ohm impedance of the scope settings?
Oh and when you touch the case in situations 2) and 3) and the noise gets canceled, can you still observe pulses? 

Let me know how it goes.

Matthias32, 2020-10-25:
Hi Oliver,

I'm still trying to figure it out: I have tried to rotate the power connector 180 degree and also used my battery powered mini scope. The issue is still there. The housing of the diode is not touching the case but the distance is very small.

I took the PCB out of the case to make sure there is no capacitance between the diode housing and the case. The only difference is that the noise signal is now a bit stronger. But again if I touch some GND via the signal disappears (while having the diode covered against light). 

I'm using some uranium glass. I just put some foam around to prevent it from rolling away all the time. The bottom side which heads to the detector is not covered.
[image]

I think I can still observe pulses when I touch the case but let me test it again to make sure.

ozel, 2020-10-28:
ok, at least we can address why you don't see alpha pulses: Uranium glass is usually not a noticable source of alpha particles. It should be in theory but in practice, the uranium concentration is so low, that you'd need to be very lucky to find a spot right on top of the surface of the glass where atoms decay and related alphas are not already absorbed by the glass. So far I have only found thoriated glass from flea markes, like these old camera lenses, to actually emit alpha partciles (besides a lot more of beta and gamma, because those lenses can be very active): https://camerapedia.fandom.com/wiki/Radioactive_lenses 
Thoriated lenses can be identified by their tainted, yellowish/brownish glass. An effect of the strong radioactivity...

Besides old smoke detectors with Am-241 sources inside (sometimes sold as "ionization chamber", *cough* Aliexpress *cough*), an easier to find and harmless kind of everyday alpha source is old ceramics featuring uranium glaze: https://www.google.com/search?q=uranium+glaze. 
Most common is this fire-red/orange kind of color. 

A less intensive alpha source, but freely available everywhere, can be collected from radon in the air of any regular room: https://iopscience.iop.org/article/10.1088/0031-9120/32/2/016/meta
In short: attach an eletrostaically charged party ballon for 15 minutes with sticky tape on a wall in a closed room (cellars work best). Release the air slowly out of the balloon without touching the surface by cutting into the balllon at the knot (if you hold the plastic firmly, it will not explode).
Then put the part of the balloon, which is opposite to the knot directly on to of the diode (but keep the thin radiation window capacitor foil in between!). 

Regarding the noise problem:
I am suprised that you see the same noise effect with the battery powered oscilloscope. That either means there is too much light reaching the diode or that you have significant EM transmission in the air around your house (or the oscilloscope itself is too noisy for these low signals or are picking up EM themsleves - but unlikely if both oscilloscpe show exactly the same noise patern. Maybe try it in a completley different building with the battery powered setup? A garden shed or outside in a *dark corner* would be ideal.

If I undestand correctly, having the case around the circuit does not make much of a difference. From this I would conclude that the ground connection between circuit and the case is not sufficient. You should have at least a short GND wire coming from PCB and soldered to the BNC connector. If that one is firmly mounted in the case it should be fine. In addition, I guess you are using at least one or two metal screws that hold the PCB in place through either the three large PCB holes or the two exposed PCB edges which are all grounded.
Could you maybe record a short video using the the batery-powerd oscillsocpe?

Looking at the uranium marble and  foam, I hope you don't expect that it is blocking the light well enough. The alpha spectrometer circuit is not yet as sensitive as a single photon-detector but really rather close to that. The light coming through the foam and marble would be by far too much if either the diode or the whole detetor setup is not kept in complete darkness.

Matthias32, 2020-10-31:
Dear Oliver,

thank you a lot for the hint. I found some uranium glaze cups on eBay. I will order them and try again. 

I changed the location but the issue was similar (see below). 

No my GND is not floating: I have soldered a wire between GND and the BNC connector and also added metal screws which connect to the two GND planes at the PCB corners. Outside the housing I have at least a wire between GND and BNC connected.

It is very strange: I have covered the diode completely with black tape and did some measurements even in nearly complete darkness. For this test I’m using a fresh diode which has still the glass cover on it so the tape can cover better (no little holes). If get closer to my working bench the noise gets worse. (Below the wooden desk there is a lot of metal) If I use the mobile scope while walking in the house the noise signal changes a lot. If I come close to some metal it gets worse. At some places the noise is nearly 0 regardless if the light is switched on or off.

[image]
(I did the test in the video also in nearly complete darkness. The result was the same)
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

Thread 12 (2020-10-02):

ozel/DIY_particle_detector #12: Code Issues

AlalaStorm, 2020-10-02:
Dear Oliver, first of all excuse me if the answer is obvious.
I'm trying to get some measurements with the electron-detector. I build it and used the web browser application to get the measurement data (named DIY_Particle_Detector_15-pulses_2020-09-06_19-51.msgp), but i'm having troubles with the data analysis.

I'm not an expert on programming with python, and I normally use the Thonny app (i'm not sure if this is a problem).
I open the analyse_and_plot_pulses.py, and write in the row 88 --> file_name = "C:/Users/Home/Desktop/DATA ANALISYS/data/DIY_Particle_Detector_15-pulses_2020-09-06_19-51.msgp"
and in the next row --> if file_name is not "C:/Users/Home/Desktop/DATA ANALISYS/data/DIY_Particle_Detector_15-pulses_2020-09-06_19-51.msgp":
Then in the row 117 --> df = pd.read_pickle("C:/Users/Home/Desktop/DATA ANALISYS/data/KCL_9-44g_1x3x3cm_touchingdiodecase_pulses_2019-07-08_23-07-18___947___11-47.pkl")
Next I run the code but I get the next message error --> 
%Run analyse_and_plot_pulses.py
Traceback (most recent call last):
  File "C:\Users\Home\Desktop\DATA ANALISYS\analyse_and_plot_pulses.py", line 117, in <module>
    df = pd.read_pickle("C:/Users/Home/Desktop/DATA ANALISYS/data/KCL_9-44g_1x3x3cm_touchingdiodecase_pulses_2019-07-08_23-07-18___947___11-47.pkl")
  File "C:\Users\Home\AppData\Roaming\Python\Python37\site-packages\pandas\io\pickle.py", line 182, in read_pickle
    return pickle.load(f) _pickle.UnpicklingError: invalid load key, 'v'.

The trouble I am facing is that I don't have enought knowledge to know what is failling and how to solve it.

Could you please give me a hand on this?
Please, let me know if I missed some information more to give you.
Thanks a lot in advance!

ozel, 2020-10-05:
Hi! 
The loading of .msgp files is at the moment implemented in a somewhat confusing way. You only need to do two things:
Set the full path name to variable `file_name` in line 88 and *comment* the line 117 such that it is disabled:
`# df = pd.read_pickle(...`. It is *either* a pickle file *or* a .mgsgp file that needs to be loaded, not both. 
The `if` statement in line 90 should not be changed at all.
I am in the process of updating this script with a more simplified loading of data files/folders and other improvements that I will hopefully upload soon. 

But in in principle, you will run into the same issue as @SteveF161 since you are using the electron-detector.
Please have a look at this reply together with my later replies here: https://github.com/ozel/DIY_particle_detector/issues/10#issuecomment-691224857
I might add a set of different pulse processing parameters (THL, min_g, min_length, max_length) that allow to process electron-detector pulses if there is more interest. Maybe Steve already found good ones?
So far I have developed the analysis scripts only with the alpha-detector in mind which produces larger output pulses that the electron-detector. 
In general, electrons from beta decays produce a continuous energy spectrum and the detector therefore cannot reveal characteristic energy lines. Unless you have a low-energy source of x-rays or mono-energetic electrons, recorded spectra will always look similar to this one from my [Sensors paper, figure 7 b)](https://www.mdpi.com/1424-8220/19/19/4264/htm):
[image]

This is not a real characteristic peak as in an alpha energy spectrum. The left edge represents the lower minimum sensitivity threshold of the amplifier circuit and the right 'edge' is defined by the geometry/thickness of the sensor chip which limits the maximum recorded energy from electrons (or scattered gammas in few cases).

I did not know about the Thonny app. It seems like a great choice especially in an education context! Since it uses a modern python version, it should work well if all required modules are installed.
I will put it on my to-do list and try it out myself. Would be great if even the `pulse_recorder.py` script runs in it.

AlalaStorm, 2020-10-06:
Hi Oliver!
Thanks a lot for your replay.
I did the changes and now i'm having the next error message:
[image: image.png]
I think now is not the same error as @SteveF161
<https://github.com/SteveF161> commented.

ozel, 2020-10-06:
It looks like something went wrong in your post, there is no error message.

But again, Steve did not really run into an "error" in this case because the `analyse_and_plot_pulses.py` script is at the moment simply not intended to be used in combination with the electron-detector. The pulses of the two detector variants have different shapes and the script is looking specifically for the shape of alpha detector pulses (unless it is changed as explained above/in the other issue).
Let me know if there is still something unclear.

closed 2020-10-20 by ozel

AlalaStorm, 2020-10-25:
Dear Oliver,
first of all thanks a lot for your support on the previous questions.

The issue I had and the one I opened in github was because of the version
of one library installed, I changed it and I got the next message:
%Run analyse_and_plot_pulses.py
analyse_and_plot_pulses.py:92: DeprecationWarning: encoding is deprecated,
Use raw=False instead.
  msgp = msgpack.unpackb(file.read(),encoding='utf-8')
                                  ts
       pulse
0   2020-10-24 19:00:37.161000+02:00  [-18792, -16099, -12613, -15855,
15239, -15793...
1   2020-10-24 19:00:37.182000+02:00  [25653, -15950, -4580, -15974, -7138,
-16140, ...
2   2020-10-24 19:00:37.199000+02:00  [-31817, 16761, -25386, 16791,
-23385, 16791, ...
3   2020-10-24 19:00:37.224000+02:00  [5186, -16432, -21696, -16444,
-12582, -16294,...
4   2020-10-24 19:00:37.237000+02:00  [-10458, -16237, -2460, -16156,
-32634, -16214...
..                               ...
         ...
285 2020-10-24 19:00:42.061000+02:00  [-1514, -15879, 11145, -15872, 28761,
-15896, ...
286 2020-10-24 19:00:42.078000+02:00  [-18351, -16214, -5046, -16487,
-25970, 16467,...
287 2020-10-24 19:00:42.095000+02:00  [-8020, 15901, 16208, -16299, 8890,
-16158, -1...
288 2020-10-24 19:22:49.557000+02:00  [-252, 17355, 6999, 17318, 25788,
16478, -1913...
289 2020-10-24 19:22:49.574000+02:00  [3105, 17338, 17731, 17398, -4991,
17333, 628,...

[290 rows x 2 columns]
detected pulses: 0 in 22 minutes -> 0.0 CPM
perr area:  [7.45484879e-05 5.97151812e+00] , perr peak:  [2.78851752e-03
6.24391592e+00]
R squared curve_fit area is:  0.9977673032941207
chi sq.: 22.876522563443515  red. chi sq.: 7.6255075211478385
R squared curve_fit peak is:  0.9999277662509872
chi sq.: 2.970503152127459  red. chi sq.: 0.9901677173758197
Traceback (most recent call last):
  File "C:\Users\Home\Desktop\DATA ANALISYS\analyse_and_plot_pulses.py",
line 392, in <module>
    max_bin = max(peaks)
ValueError: max() arg is an empty sequence

I was kind of surprised for two reasons:
First, I was expecting some graphics instead of this. Is it correct that
type of result? Should I now process those values with some kind of data
editor to obtain a graph?

Second, as you can see in the message obtained (detected pulses: 0 in 22
minutes -> 0.0 CPM). I did the same experiment 4 times with different
exposition times. From some minutes to 3 hours, but I'm still getting 0
detected pulses. I'm wondering which could be the error I am making.
The setup I'm using is the one on the attached photos (1, 2 and 3). Then I
open the web browser application and it seems is getting something photo
4), I switch on the button to connect the battery and start with the
measurements (photo 5) but nothing more than a flat line is in the screen
(the number in sum and e- are moving high), if I turn off the battery
button I get one more time this noise (photo 6) with the numbers going up.

So I am sure, I'm doing something wrong but I have no Idea what...
Maybe the banana position? Some connection with the hardware?
Which is the timescale in which I should take measurements to get the
electron detection? Minutes, hours, ...?

So, one more time, lots of thanks for your support!
I was very excited to do this project but I'm facing trouble with every
step... soldering (I didn't know before), programming with python, ... So
for me is kind of motivating having your feedback.

[image: WhatsApp Image 2020-10-25 at 09.19.25 (1).jpeg]
[image: WhatsApp Image 2020-10-25 at 09.19.25.jpeg][image: WhatsApp Image
2020-10-25 at 09.40.04.jpeg]

[image: WhatsApp Image 2020-10-25 at 09.40.04 (1).jpeg]

[image: WhatsApp Image 2020-10-25 at 09.40.05.jpeg]

[image: WhatsApp Image 2020-10-25 at 09.40.05 (1).jpeg]

ozel, 2020-10-28:
Hi, I am glad that you like the project so much.
There are multiple things here:
The script does not find pulses, thats why it stops with an error. But it reads the file that you have recorded correctly. 
As I wrote above - and I would really encourage you to read my answers above carefully again - the electron-detector that you have built is not compatible with that python script. There are practical reasons: different pusles sizes of electron-detector and the alpha-spectrometer, this could be addressed but needs *changes* in the script - see my previous replys above. 
But there is also an important "*physics reason*": it is not possible to record a meaningfull energy spectrum from just electrons from beta decays with the electron-detector that you have built. 
If you want to record and plot alpha energy spectra like shown in my paper, you can change a few components which will turn the detetcor into an alpha-spectrometer: D1-4, R3, R4, R5, R8, C4, C6, C9 need to be changed.
More on both detector variants, including the different part lists: https://github.com/ozel/DIY_particle_detector/wiki/Assembly-Instructions#required-parts

Unfortunatelly, there are again no images visible in your post.
But you mention measuring a bananna. The radioactivity of one banana is extremly low because the amount of potassium-40 in it is very low, too. Most detectors cannot measure this low level, you would need an expensive gamma spectrometer that is well shielded with lead against background radiation. I know this sounds unexpected because so many talks about the radioactivity of a banana -  it is over-hyped on youtube and actually hard to measure.

In a nutshell, you are not doing things wrong per se. You are just trying to measure something that cannot be measured with this detector. 
I would propsose to find some reliable reference object like old uranium glass or uranium galzed ceramics from the flea markets or with some luck from the vintage glass cupboard of your parents/grandparents (check google and wikipedia for images of "uranium glass" and "uranium glaze").  From those objects, you could expect a few pulses per minute, like 3 to 10, maybe, depending on the object, of course. 
From just the terrestrial and cosmic natural radiation - without any source on the detector- the count rate is very low because the diodes are rather small. It depends on your location, but it would typically be something like one pulse every 5 minutes.
Alternatively, you can try to find potassium salt in a supermarket or organics/diet food shop and measure that: KCl. That is basically 50 percent of potassium and much more of the radioactive and naturally occurring potassium-40. An English brand of KCl, aka "reduced sodium slat", is called "No Salt" (100 % KCl) and another one "Lo Salt" (66% KCl). Pharmacies and eBay sell KCl as well.

By the way, the script output tells me that your recording was 290 waveforms in 22 minutes. That is way too much just from natural background radiation if you had just a banana on the detetcor. But again, your pictures are missing. Maybe you were measuring something else than a banana. Maybe try posting your pictures from another browser?

I suspect that the threshold level is set too sensitive and your are recording too much noise instead of actual pulses from radioactivity. That means you have to move the threshold line further down, away from the signal noise.
Please have a close look at the troubleshooting page on the wiki: https://github.com/ozel/DIY_particle_detector/wiki/Troubleshooting
If your pulses do not look like those, you most probably measure just electronic noise.

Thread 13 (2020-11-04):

### ISSUE TITLE
Wrong part numbers sent to KitSpace for 1M resistor

### ISSUE THREAD

**Issue by SteveF161** [ozel/DIY_particle_detector#13]
Hi Oliver

I've started to build the alpha detector and I've hit a problem (No, not soldering the SMD, though that did cause a certain amount of frustration!). I ordered all the parts through KitSpace and Farnell but when my son and I got to R5, it was nowhere to be seen. It's in the KitSpace manifest but, as you can see from the screenshot, the part number seems to be for a 100k resistor.

Steve
![WrongPart](https://user-images.githubusercontent.com/28903476/97084977-59fe6a00-1612-11eb-88cb-7c5442d18194.png)

**Comment by ozel** [comment]
Hi Steve, thanks for pointing this out! I've corrected the part number for R5 at Farnell in the alpha-spectrometer file in 010041b1e182f9f5b558d1ccba435b52a0fc5777.
It should be reflected on Kitspace with the next automatic sync or when @kasbah runs a manual update.
There other order codes for Mouser etc. were correct, I've just updated a few more alternatives according to current parts availability.

Congratulations on soldering the SMD part. I know it's hard for the first time, tweezers and patients definitly go a long way there.
At least you and your son may now have a better feeling how on earth our modern consumer electronics devices can be so small and capabable at the same time. :-)

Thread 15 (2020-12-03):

ozel/DIY_particle_detector #15: MALAS DETECCIONES DETECTORES ALFA Y BETA

josepanglada6, 2020-12-03:
Hola buenas,
Compré los dos dispositivos (alfa y beta) y monté las placas electrónicas y hice una caja de aluminio con una ventana de radiación que se protege con cinta adhesiva metálica.
Pero cuando abro un programa como Becqmoni o alguna página web de osciloscopio, solo me marca detecciones cuando doy golpes en la placa o en el cable de sonido. Si acerco elementos radioactivos no hace nada. A qué puede ser debido esto? Que programas se recomiendan? Es necesario colocar otro tipo de cinta en la ventana de radiación?
Gracias.

ozel, 2020-12-08:
Hello, 
I had to translate the question since I do not speak Spanish.
Please consider posting in English.

To get your detectors running, please have a look at the Troubleshooting page in the wiki:
https://github.com/ozel/DIY_particle_detector/wiki/Troubleshooting
If you use the audio/microphone input of a Laptop, you probably have to change the microphone volume setting in Windows. Sometimes with headset connectors, it should be between 50% and 75% to work properly, this depends on your computer.
Also check that you have the correct cable for your computer:
https://github.com/ozel/DIY_particle_detector/wiki/Cables#audio-jack-connector-overview-35-mm-trstrrs
If you use the same low-cost soundcard as me, the CM 108, the input volume should be set at 100% with extra microphone boost/gain enabled:
https://github.com/ozel/DIY_particle_detector/wiki/Soundcards

josepanglada6, 2020-12-09:
Thanks for the interest Ozel. 

I have two questions for the alpha detector:
When I use the application Becqmoni in order to study the detections, if I apply the formula that is said on the web for the energy calibration, I get some detections with negative energy. Is this correct?https://github.com/ozel/DIY_particle_detector/wiki/Energy-Spectra#energy-calibration 

On the other hand, I have no idea how to use this python script: https://github.com/ozel/DIY_particle_detector/blob/master/data_analysis_and_reference_measurements/diode_detector/analyse_and_plot_pulses.py 
I have downloaded the program annaconda. Then, it represents that I have to copy all the python script adding on it the file name and something else? I have to copy all the script or I have to delet the clarifications, the instructions of the beggining...? And where do I have to copy the script? 
If you could explain me how this works I would appreciate it.

Thanks, Josep.

ozel, 2020-12-09:
Hi Josep,

I have split your questions up into two posts in the brand new Discussions feature of Github!
Please follow these links: #18 #20 
I will close this issue later.

Cheers,
Oliver

closed 2020-12-14 by ozel

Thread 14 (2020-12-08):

### ISSUE TITLE
Please mention capacitor properities

### ISSUE THREAD

**Issue by UweBonnes** [ozel/DIY_particle_detector#14]
Hello,

without hints in the BOM, people will tend to buy Y or even Z type ceramic capacitors at least for the high capacitance values , 100 n C3 and C7 and  470 n C4. Y/Z are know for microphonic and other bad effect, and at least  C3, C7 and C4 should be of X or even COG quality. 100 nF COG is not cheap, but achievable. With C4 -> 100 n, R4 > 22k, R5 -> 4M7 and C6 -> 680 p, all C3, C7 and C7 could be specified as 100 nF/COG. Otherwise bothe bias dividers R1,R2,R6 and R7 could be made 10 time higher without bad influence but extend battery lifetime.

Please at least state in the BOM that Y/Z ceramics is deprecated and COG for C3/C7 is preferred.

**Comment by ozel** [comment]
Hi Uwe,

thanks for your comments related to the alpha-spectrometer variant.
On a first note, I guess you must have missed the bom folder. The two .csv files there feature specific parts with order codes for the suppliers listed on the related kitspace site of the project: 
https://kitspace.org/boards/github.com/ozel/diy_particle_detector/alpha-spectrometer/ 

For the large C4, I actually went with a Z type. C1 and C2 are of course C0G, but for the others (selected X and Y types), I doubt that it matters enough in terms of SNR performance and variances in the energy response. However, I am happy to reconsider if you have noticed improvements with other choices - please let me know!

Since the alpha-spectrometer variant of the circuit does actually exhibit quite some microphonic effect, I had replaced all capacitors of C0G types as a test. But since that did not reduce the microphonics, I concluded the PIN diode itself must be coupling capacitively with the soft tin metal walls which in turn pick up vibrations easily (this does not happen with thick-walled aluminum die-cast cases as explained in the Wiki).
I would be curious to know if you did a similar capacitor comparison in this circuit and noticed improvements.
Did you run into problems with reusing my energy calibration as described in the corresponding paper and the Wiki?

Regarding the general choice of parts: This project is really geared towards electronic beginners and high-school level physics teaching environments where people are often not experienced tinkerers. Therefore I tried to keep the overall amount of parts as well as the number of different resistor/capacitor values as low as possible.

For a detector signal processing expert, the choice of time constants after the first stage may look unusual. But they are on purpose in order to decrease the rise time of the first edge as well as keeping the complete pulse as bipolar as possible while maintaining large enough SNR and pulse width (at an overall low number of components). 
Without the extra slowing down, widening, and 'bi-polarisation' of the pulse, certain headset sockets will detect it as an unexpected glitch and switch off the sound input. The circuit is trying to emulate a microphone signal after all which can be sampled well at 48 kHz.

Regarding the bias resistors, I thought about increasing them but eventually kept them low in favor of reducing the number of different resistors (10k and 4k7 are reused). Their fraction of the current consumption is only 20%, the majority is consumed by the opamps. In general, I am recommending to use good old 9V NIMH accumulators, c.f. the Wiki.

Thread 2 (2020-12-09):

### ISSUE TITLE
Part Selection

### ISSUE THREAD

**Issue by Tcub** [ozel/DIY_particle_detector#2]
Question about the part selection. 

Where the through holes chosen due to ease of assembly? I.e. there would be no issue swapping them out for SMD parts would there? (I don't think there would be an issue but I thought it worth just asking)

**Comment by ozel** [comment]
Absolutely! SMD parts, 0805 in particular, work really well on top of the 2.5 mm through-hole footprints. (I've used sometimes 100 nF 0805 if you look closely in the pictures)

The preferred bills of material - as featured with order codes from 4 major suppliers on kitspace.org - focuses on through-hole parts to make it easier for beginners:
https://kitspace.org/boards/github.com/ozel/diy_particle_detector/alpha-spectrometer/
https://kitspace.org/boards/github.com/ozel/diy_particle_detector/electron-detector/

In case of 40 mega Ohm/R3 for the alpha-spectrometer, I've selected an SMD part since it is slightly better noise-wise and through-hole resistors with such high values seem harder to get. 

I'll leave this open for others to ask part related questions.

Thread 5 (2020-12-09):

### ISSUE TITLE
Physics properties of the detectors

### ISSUE THREAD

**Issue by cjnqt** [ozel/DIY_particle_detector#5]
this is a cool application!

What causes the upper energy range detection limit of ~8 MeV? Is it caused by the amplification range? The diode itself?

**Comment by ozel** [comment]
the diode itself can only provide measurable ionization within its depleted space-charge region (which is proportional to a volume since the sensitive area remains constant). this is a function of the applied bias voltage (see figure 3b in https://www.mdpi.com/1424-8220/19/19/4264/htm) and of course geometrical/physical doping limitations of the diode chip. Ref. 20 of the article suggests that the maximum depleted depth would be somewhere below 100 micrometers.

I calibrated the detector with some low-energy artificial radionuclides and then tested it with natural alpha emitters which go up to about 8.8 MeV max. (polonium-212) - c.f. the article. So for that energy range, it is proven that the energy calibration of the amplifier circuit is correct and linear as described. I could be as well linear for higher energies (and it would work in principle if the bias voltage is increased somewhat) but then you would need to stick it into a particle accelerator beamline, so it is not really relevant for measuring natural radioactivity and neither for artificially created fission products of nuclear reactors, those alpha-emitting isotopes are all within the 8/9 MeV upper range value. 

Another aspect is the input voltage range of the soundcard, larger signals than the ones I tested could saturate them depending on specific soundcard properties. An oscilloscope would not have that limitation but usually has a lower amplitude (y-axis) resolution than the 16-bit of a soundcard/laptop/mobile microphone input.

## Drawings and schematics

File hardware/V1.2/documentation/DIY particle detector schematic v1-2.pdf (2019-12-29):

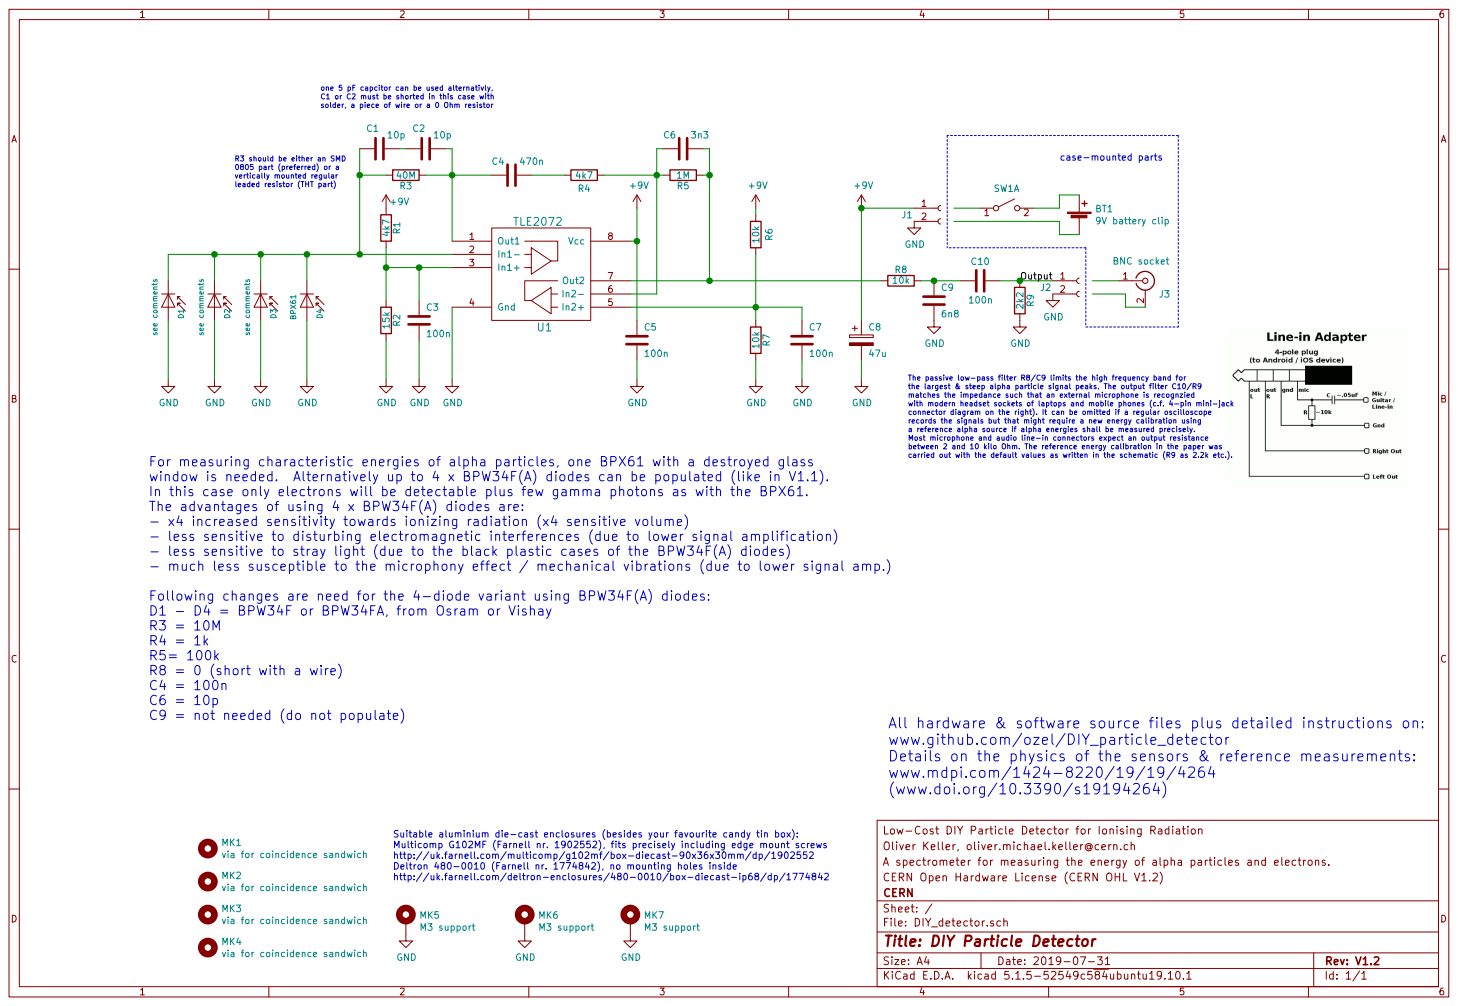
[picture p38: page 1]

one 5 pF capcitor can be used alternativly, C1 or C2 must be shorted in this case with solder, a piece of wire or a 0 Ohm resistor

0805 part (preferred) or a vertically mounted regular

The passive low-pass filter R8/C9 limits the high frequency band for
the largest & steep alpha particle signal peaks. The output filter C10/R9 matches the impedance such that an external microphone is recognzied with modern headset sockets of laptops and mobile phones (c.f. 4-pin mini-jack connector diagram on the right). It can be omitted if a regular oscilloscope records the signals but that might require a new energy calibration using a reference alpha source if alpha energies shall be measured precisely. Most microphone and audio line-in connectors expect an output resistance between 2 and 10 kilo Ohm. The reference energy calibration in the paper was carried out with the default values as written in the schematic (R9 as 2.2k etc.).

For measuring characteristic energies of alpha particles, one BPX61 with a destroyed glass
In this case only electrons will be detectable plus few gamma photons as with the BPX61.
The advantages of using 4 x BPW34F(A) diodes are:
- x4 increased sensitivity towards ionizing radiation (x4 sensitive volume)
- less sensitive to disturbing electromagnetic interferences (due to lower signal amplification)
- less sensitive to stray light (due to the black plastic cases of the BPW34F(A) diodes)
- much less susceptible to the microphony effect / mechanical vibrations (due to lower signal amp.)

Following changes are need for the 4-diode variant using BPW34F(A) diodes:
D1 - D4 = BPW34F or BPW34FA, from Osram or Vishay
R8 = 0 (short with a wire)
C9 = not needed (do not populate)

www.github.com/ozel/DIY_particle_detector
Details on the physics of the sensors & reference measurements:
www.mdpi.com/1424-8220/19/19/4264
(www.doi.org/10.3390/s19194264)

Low-Cost DIY Particle Detector for Ionising Radiation MK3

Suitable aluminium die-cast enclosures (besides your favourite candy tin box):
Multicomp G102MF (Farnell nr. 1902552), fits precisely including edge mount screws
http://uk.farnell.com/multicomp/g102mf/box-diecast-90x36x30mm/dp/1902552
Deltron 480-0010 (Farnell nr. 1774842), no mounting holes inside
http://uk.farnell.com/deltron-enclosures/480-0010/box-diecast-ip68/dp/1774842

Oliver Keller, oliver.michael.keller@cern.ch
A spectrometer for measuring the energy of alpha particles and electrons.
CERN Open Hardware License (CERN OHL V1.2)
File: DIY_detector.sch Sheet: / CERN

via for coincidence sandwich

Id: 1/1 Title: DIY Particle Detector

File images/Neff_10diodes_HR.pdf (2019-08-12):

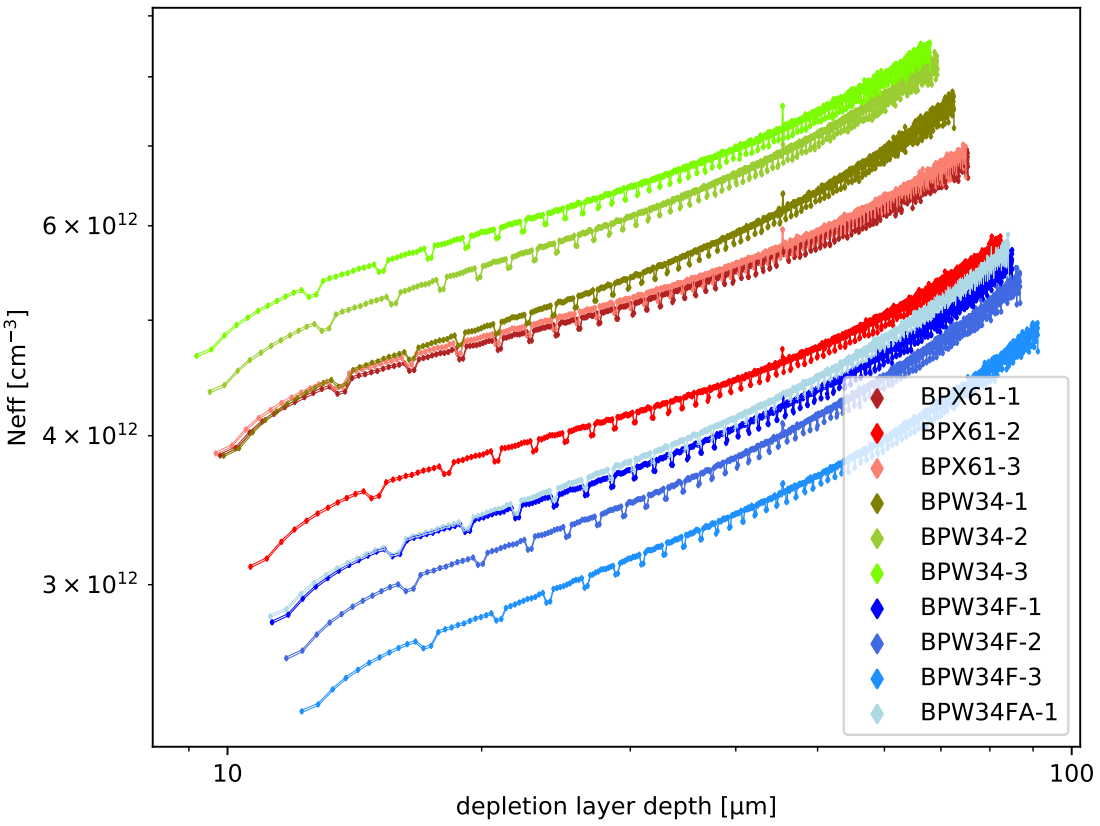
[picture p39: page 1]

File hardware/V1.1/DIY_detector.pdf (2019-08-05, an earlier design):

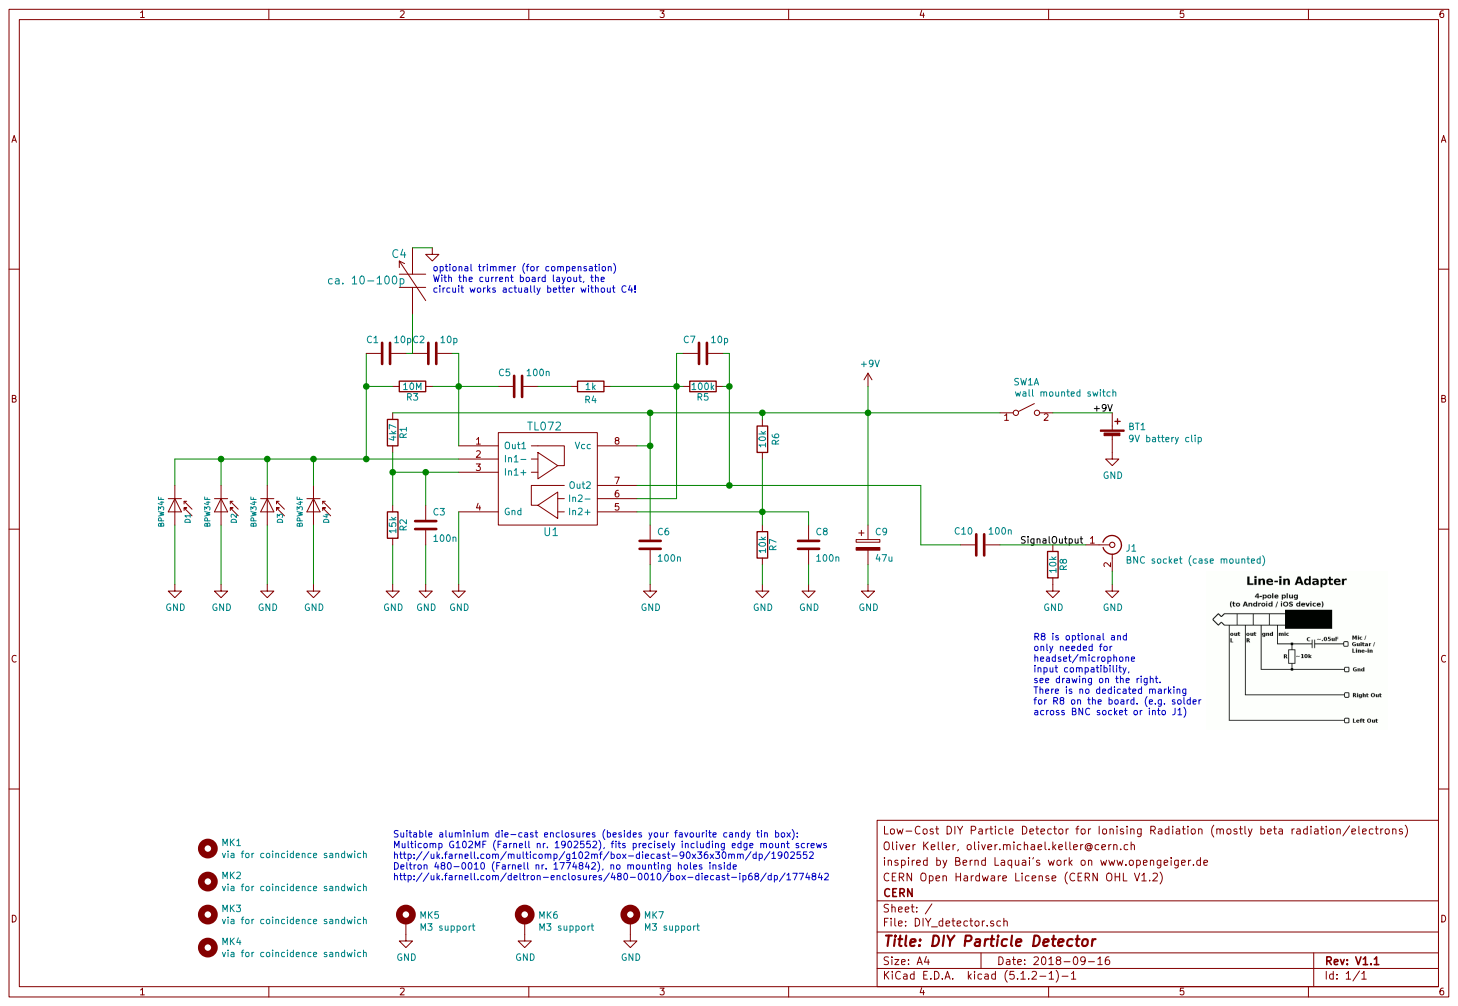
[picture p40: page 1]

optional trimmer (for compensation)
With the current board layout, the

Low-Cost DIY Particle Detector for Ionising Radiation (mostly beta radiation/electrons) C9

across BNC socket or into J1) GND

R8 is optional and
only needed for
headset/microphone
input compatibility,
see drawing on the right.
There is no dedicated marking
for R8 on the board. (e.g. solder

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

Oliver Keller, oliver.michael.keller@cern.ch
inspired by Bernd Laquai's work on www.opengeiger.de
CERN Open Hardware License (CERN OHL V1.2)
File: DIY_detector.sch Sheet: / CERN

via for coincidence sandwich MK2

via for coincidence sandwich MK3

via for coincidence sandwich MK4

Id: 1/1 Title: DIY Particle Detector

via for coincidence sandwich

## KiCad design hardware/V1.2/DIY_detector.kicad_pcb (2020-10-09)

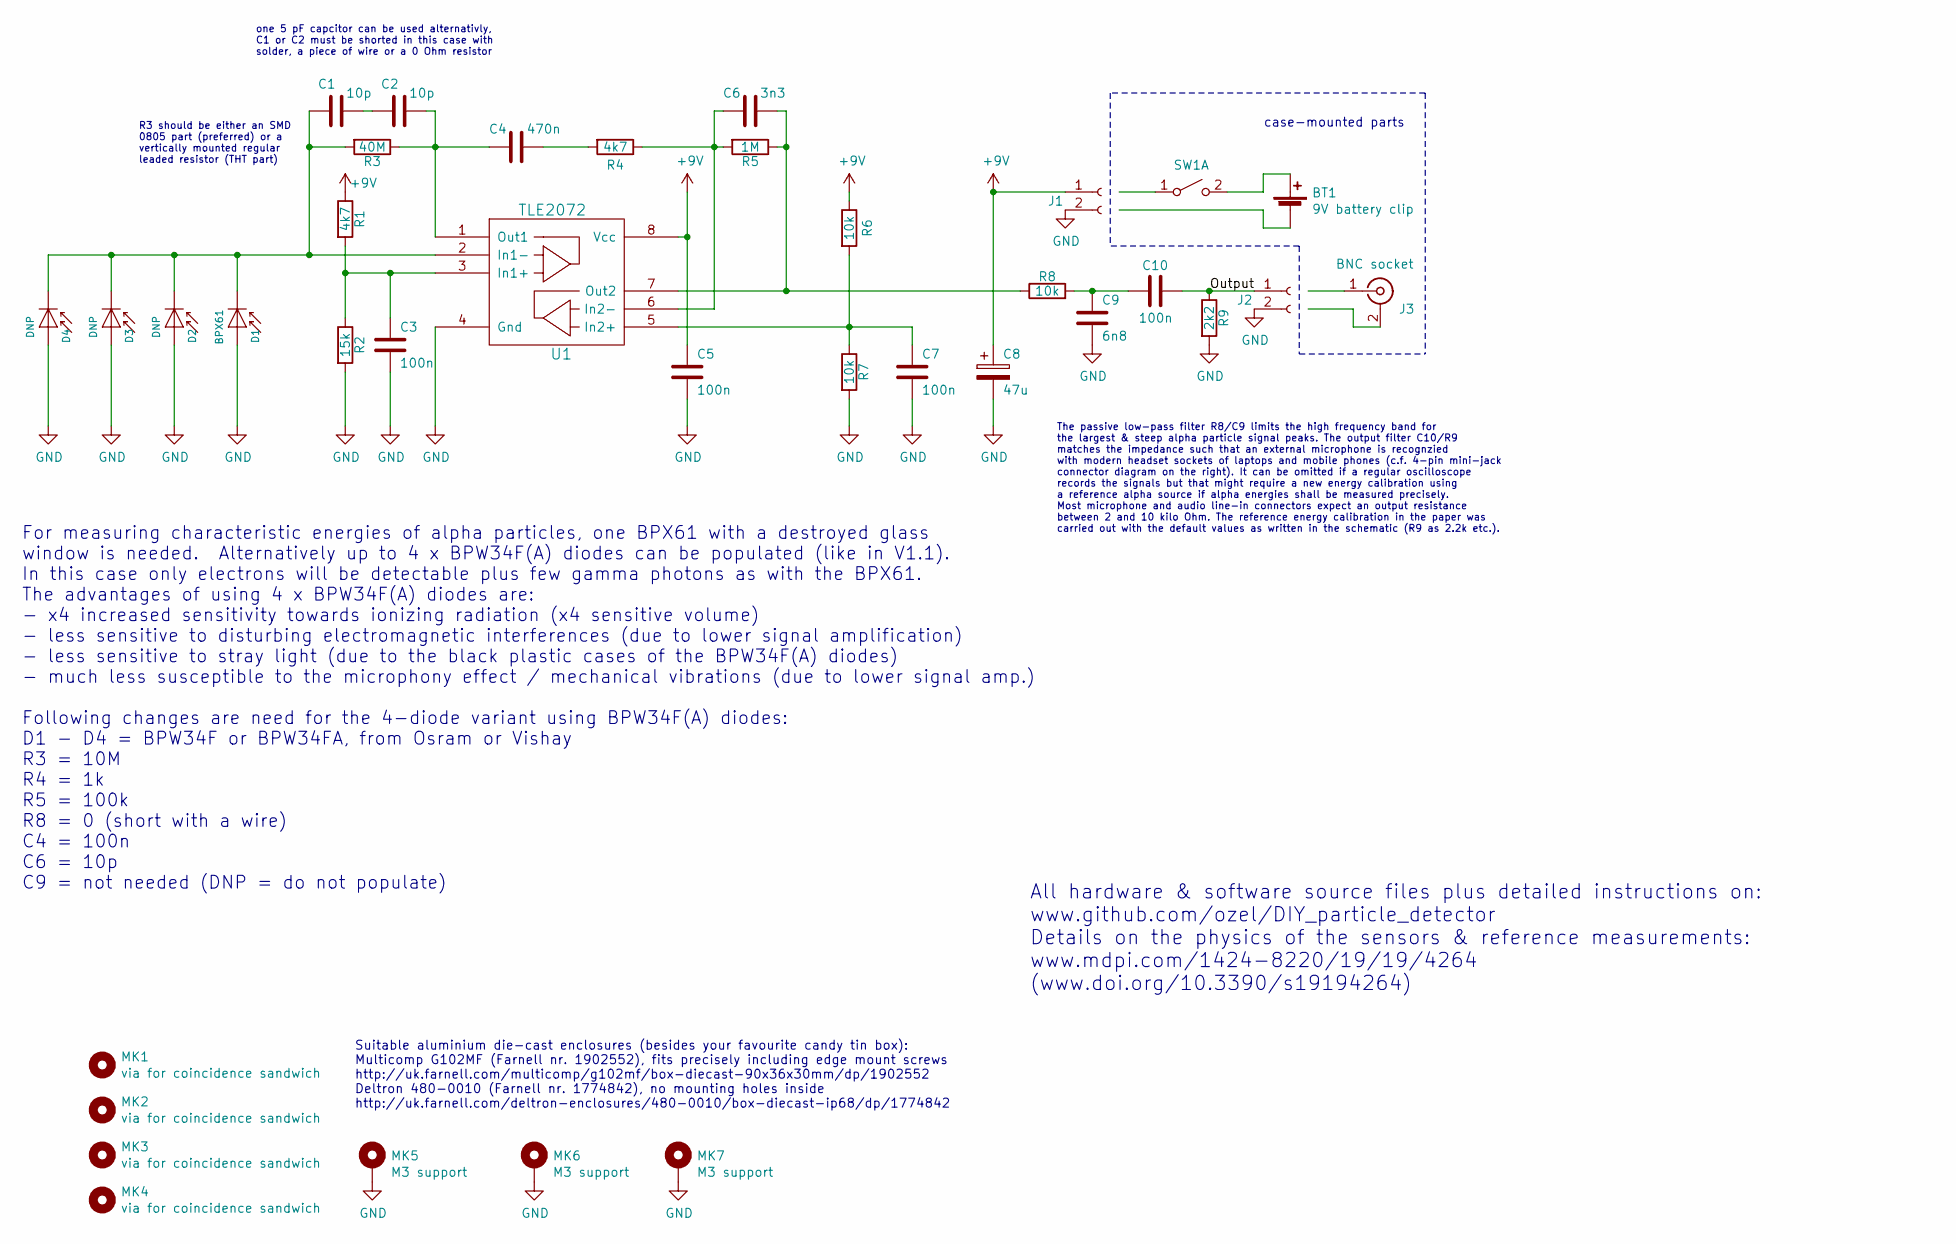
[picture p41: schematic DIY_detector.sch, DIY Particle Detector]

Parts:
BT1: 9V battery clip; MFG_PN FC6830; FARNELL 2817539
C1, C2: 10p; C_Disc_D3.0mm_W1.6mm_P2.50mm; MFG_PN MC0805N100J101A2.54MM; FARNELL 1694175
C3, C5, C7, C10: 100n; C_Disc_D3.0mm_W1.6mm_P2.50mm; MFG_PN MC0805Y104M500A2.54MM; FARNELL 2112751
C4: 470n; C_Disc_D3.0mm_W1.6mm_P2.50mm; MFG_PN C320C474M5U5TA; FARNELL 1457660
C6: 3n3; C_Disc_D3.0mm_W1.6mm_P2.50mm; MFG_PN TS170R1H332KSBBA0R; FARNELL 2901293
C8: 47u; CP_Radial_D6.3mm_P2.50mm; MFG_PN ECA-1JHG470; FARNELL 9693033
C9: 6n8; C_Disc_D3.0mm_W1.6mm_P2.50mm; MFG_PN TS170R1H682KSBBA0R; FARNELL 2901297
D1: BPX61; PhotoDiode_DIL2_4.3x4.65_RM5.08; MFG_PN BPW34F/FA; FARNELL 2981621
D2, D3: DNP; PhotoDiode_DIL2_4.3x4.65_RM5.08; MFG_PN BPW34F/FA; FARNELL 2981621
D4: DNP; PhotoDiode_DIL2_4.3x4.65_RM5.08; MFG_PN BPX61; FARNELL 2981630
J1, J2: Conn_01x02_Female; Pin_Header_Straight_1x02_Pitch2.54mm
J3: BNC socket; MFG_PN 13-25; FARNELL 1169699
MK1, MK2, MK3, MK4: via for coincidence sandwich; SolderWirePad_single_0-8mmDrill
MK5, MK6, MK7: M3 support; MountingHole_3.2mm_M3_ISO7380_Pad
R1, R4: 4k7; R_Axial_DIN0207_L6.3mm_D2.5mm_P7.62mm_Horizontal; MFG_PN MCMF006FF4701A50; FARNELL 2401772
R2: 15k; R_Axial_DIN0207_L6.3mm_D2.5mm_P7.62mm_Horizontal; MFG_PN MCMF006FF1502A50; FARNELL 2401785
R3: 40M; R_Axial_DIN0204_L3.6mm_D1.6mm_P2.54mm_Vertical; MFG_PN RH73H2A40MKTN; FARNELL 1174521
R5: 1M; R_Axial_DIN0207_L6.3mm_D2.5mm_P7.62mm_Horizontal; MFG_PN MCMF006FF1004A50; FARNELL 2401807
R6, R7, R8: 10k; R_Axial_DIN0207_L6.3mm_D2.5mm_P10.16mm_Horizontal; MFG_PN MCMF006FF1002A50; FARNELL 2401780
R9: 2k2; R_Axial_DIN0207_L6.3mm_D2.5mm_P10.16mm_Horizontal; MFG_PN MCMF006FF2201A50; FARNELL 2401780
SW1: -; MFG_PN 1MS1T1B1M1QE; FARNELL 9473416
U1: TLE2072; DIP-8_W7.62mm_LongPads; MFG_PN TLE2072ACP; FARNELL 3117956

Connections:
+9V: C5.1, C8.1, J1.1, R1.1, R6.1, U1.8 (Vcc)
/Output: C10.2, J2.1, R9.1
GND: C3.2, C5.2, C7.2, C8.2, C9.2, D1.2 (A), D2.2 (A), D3.2 (A), D4.2 (A), J1.2, J2.2, MK5.1, MK6.1, MK7.1, R2.2, R7.2, R9.2, U1.4 (Gnd)
unnamed: BT1.1 (+), SW1.2 (B)
unnamed: C1.1, D1.1 (K), D2.1 (K), D3.1 (K), D4.1 (K), R3.2, U1.2 (In1-)
unnamed: C1.2, C2.1
unnamed: C2.2, C4.1, R3.1, U1.1 (Out1)
unnamed: C3.1, R1.2, R2.1, U1.3 (In1+)
unnamed: C4.2, R4.2
unnamed: C6.1, R4.1, R5.2, U1.6 (In2-)
unnamed: C6.2, R5.1, R8.1, U1.7 (Out2)
unnamed: C7.1, R6.2, R7.1, U1.5 (In2+)
unnamed: C9.1, C10.1, R8.2

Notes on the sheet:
one 5 pF capcitor can be used alternativly, C1 or C2 must be shorted in this case with solder, a piece of wire or a 0 Ohm resistor
Suitable aluminium die-cast enclosures (besides your favourite candy tin box): Multicomp G102MF (Farnell nr. 1902552), fits precisely including edge mount screws http://uk.farnell.com/multicomp/g102mf/box-diecast-90x36x30mm/dp/1902552 Deltron 480-0010 (Farnell nr. 1774842), no mounting holes inside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
For measuring characteristic energies of alpha particles, one BPX61 with a destroyed glass window is needed. Alternatively up to 4 x BPW34F(A) diodes can be populated (like in V1.1). In this case only electrons will be detectable plus few gamma photons as with the BPX61. The advantages of using 4 x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
The passive low-pass filter R8/C9 limits the high frequency band for the largest & steep alpha particle signal peaks. The output filter C10/R9 matches the impedance such that an external microphone is recognzied with modern headset sockets of laptops and mobile phones (c.f. 4-pin mini-jack connecto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
case-mounted parts
R3 should be either an SMD 0805 part (preferred) or a vertically mounted regular leaded resistor (THT part)
All hardware & software source files plus detailed instructions on: www.github.com/ozel/DIY_particle_detector Details on the physics of the sensors & reference measurements: www.mdpi.com/1424-8220/19/19/4264 (www.doi.org/10.3390/s19194264)

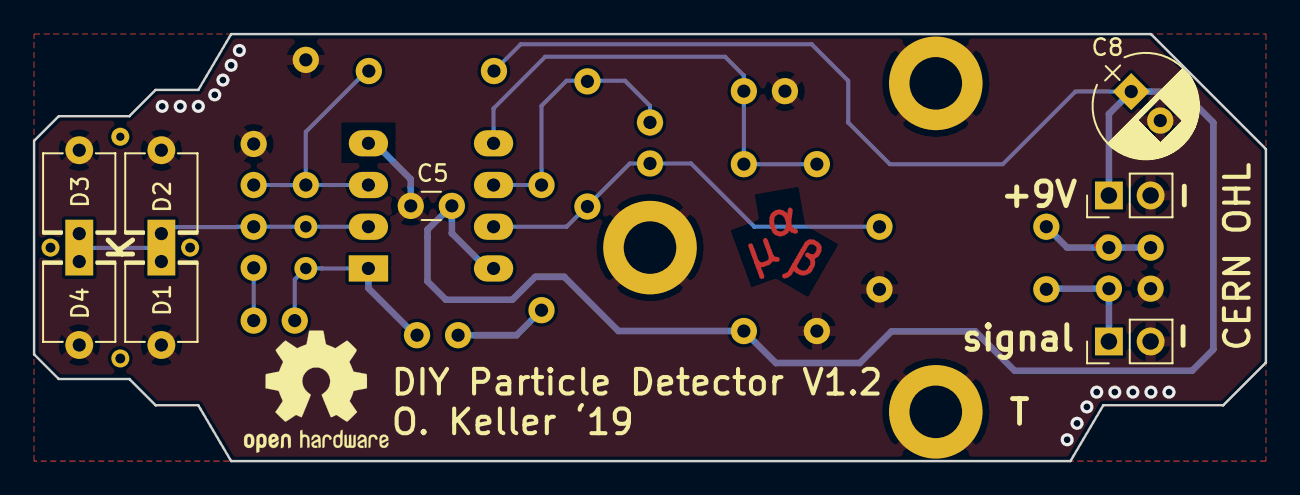
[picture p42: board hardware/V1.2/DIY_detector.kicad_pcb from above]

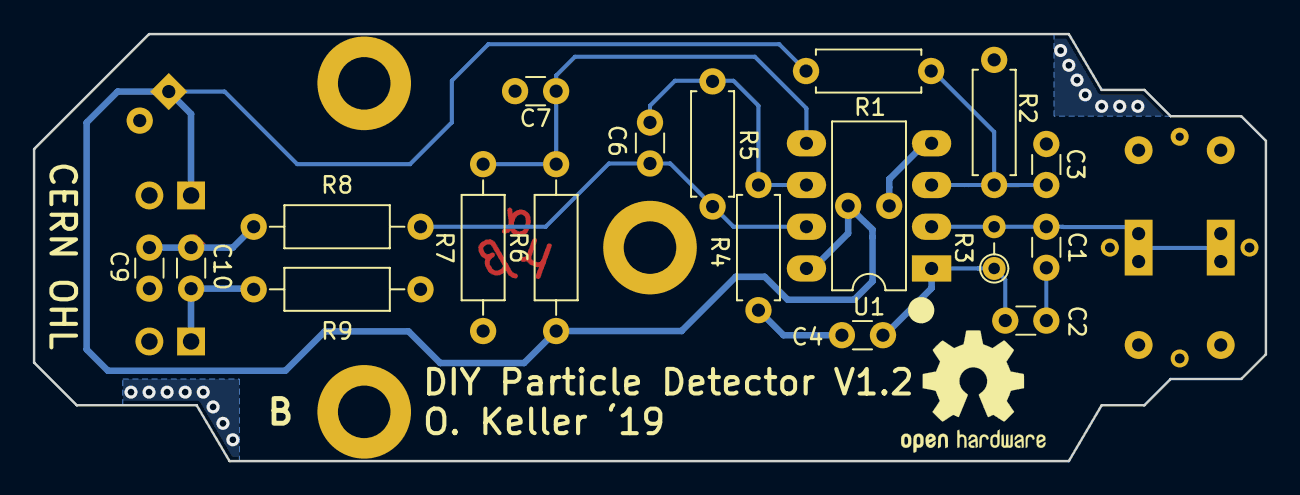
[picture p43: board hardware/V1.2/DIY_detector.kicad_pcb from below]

Board: 2 copper layers, 75.0 x 26.0 mm, 33 parts (18 on the bottom side), 12 nets.

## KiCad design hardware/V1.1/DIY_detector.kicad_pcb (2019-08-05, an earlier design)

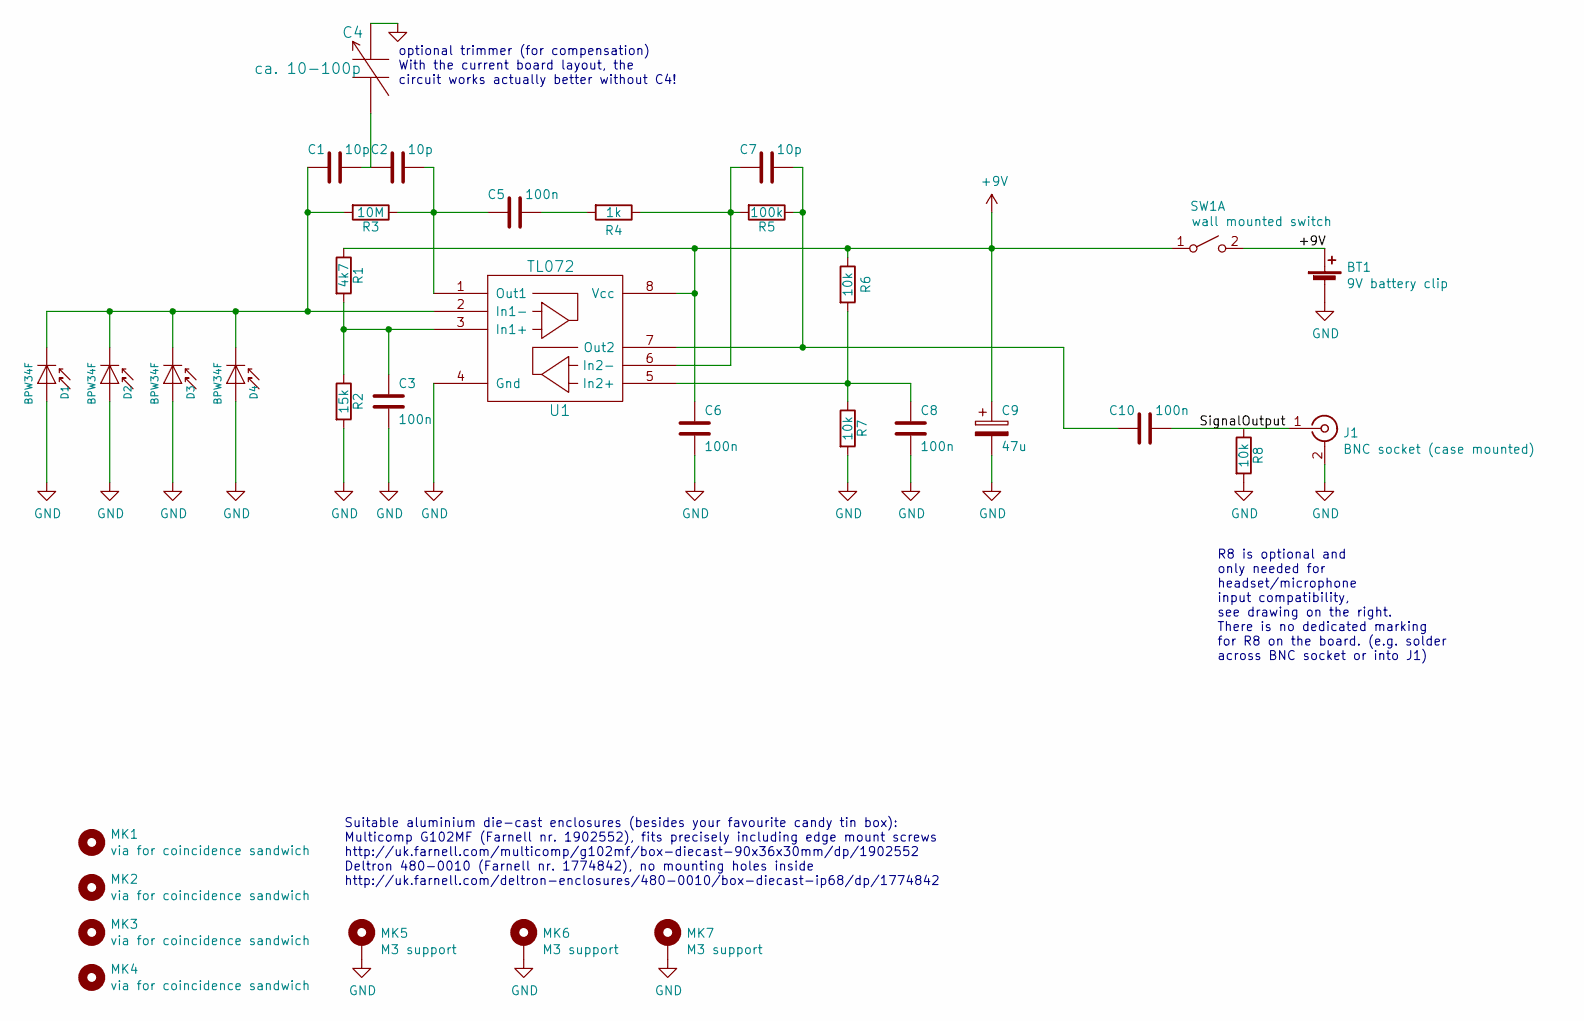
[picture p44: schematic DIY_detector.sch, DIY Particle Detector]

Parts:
BT1: 9V battery clip; Pin_Header_Straight_1x02_Pitch2.54mm; MFG_PN FC6830
C1, C2, C7: 10p; C_Disc_D3.0mm_W1.6mm_P2.50mm; MFG_PN MC0805N100J101A2.54MM
C3, C5, C6, C8, C10: 100n; C_Disc_D3.0mm_W1.6mm_P2.50mm; MFG_PN MC0805Y104M500A2.54MM
C4: ca. 10-100p; C_Trimmer_Murata_TZB4-B; MFG_PN TZB4P400AB10R00
C9: 47u; CP_Radial_D6.3mm_P2.50mm; MFG_PN ECA1JM470
D1, D2, D3, D4: BPW34F; PhotoDiode_DIL2_4.3x4.65_RM5.08; MFG_PN BPW34 F(A)
J1: BNC socket (case mounted); Pin_Header_Straight_1x02_Pitch2.54mm; MFG_PN 13-25
MK1, MK2, MK3, MK4: via for coincidence sandwich; SolderWirePad_single_0-8mmDrill
MK5, MK6, MK7: M3 support; MountingHole_3.2mm_M3_ISO7380_Pad
R1: 4k7; R_Axial_DIN0207_L6.3mm_D2.5mm_P7.62mm_Horizontal; MFG_PN MCMF006FF4701A50
R2: 15k; R_Axial_DIN0207_L6.3mm_D2.5mm_P7.62mm_Horizontal; MFG_PN MCMF006FF1502A50
R3: 10M; R_Axial_DIN0204_L3.6mm_D1.6mm_P2.54mm_Vertical; MFG_PN MCMF006FF1005A50
R4: 1k; R_Axial_DIN0207_L6.3mm_D2.5mm_P7.62mm_Horizontal; MFG_PN MCMF006FF1001A50
R5: 100k; R_Axial_DIN0207_L6.3mm_D2.5mm_P7.62mm_Horizontal; MFG_PN MCMF006FF1003A50
R6, R7, R8: 10k; R_Axial_DIN0207_L6.3mm_D2.5mm_P10.16mm_Horizontal; MFG_PN MCMF006FF1002A50
SW1: wall mounted switch; MFG_PN 1MS1T1B1M1QE
U1: TL072; DIP-8_W7.62mm_LongPads; MFG_PN TL072ACP

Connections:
+9V: BT1.1 (+), C6.1, C9.1, R1.1, R6.1, SW1.1 (A), SW1.2 (B), U1.8 (Vcc)
/Output: C10.2, J1.1 (In)
GND: BT1.2 (-), C3.2, C4.2, C6.2, C8.2, C9.2, D1.2 (A), D2.2 (A), D3.2 (A), D4.2 (A), J1.2 (Ext), MK5.1, MK6.1, MK7.1, R2.2, R7.2, R8.2, U1.4 (Gnd)
unnamed: C1.1, D1.1 (K), D2.1 (K), D3.1 (K), D4.1 (K), R3.2, U1.2 (In1-)
unnamed: C1.2, C2.1, C4.1
unnamed: C2.2, C5.1, R3.1, U1.1 (Out1)
unnamed: C3.1, R1.2, R2.1, U1.3 (In1+)
unnamed: C5.2, R4.2
unnamed: C7.1, R4.1, R5.2, U1.6 (In2-)
unnamed: C8.1, R6.2, R7.1, U1.5 (In2+)
unnamed: C7.2, C10.1, R5.1, U1.7 (Out2)

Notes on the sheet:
optional trimmer (for compensation) With the current board layout, the circuit works actually better without C4!
R8 is optional and only needed for headset/microphone input compatibility, see drawing on the right. There is no dedicated marking for R8 on the board. (e.g. solder across BNC socket or into J1)
Suitable aluminium die-cast enclosures (besides your favourite candy tin box): Multicomp G102MF (Farnell nr. 1902552), fits precisely including edge mount screws http://uk.farnell.com/multicomp/g102mf/box-diecast-90x36x30mm/dp/1902552 Deltron 480-0010 (Farnell nr. 1774842), no mounting holes inside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

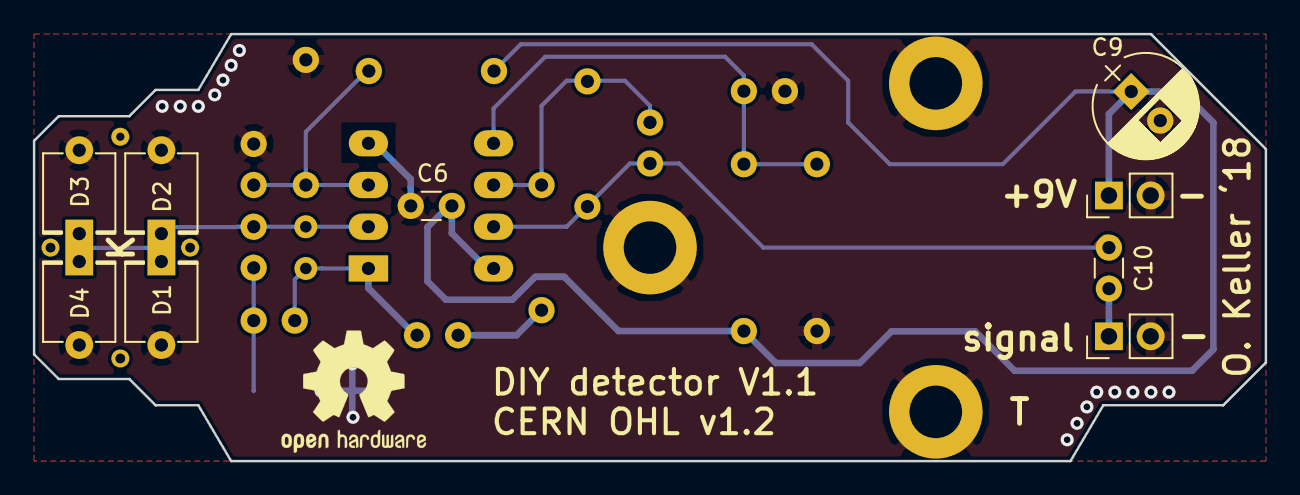
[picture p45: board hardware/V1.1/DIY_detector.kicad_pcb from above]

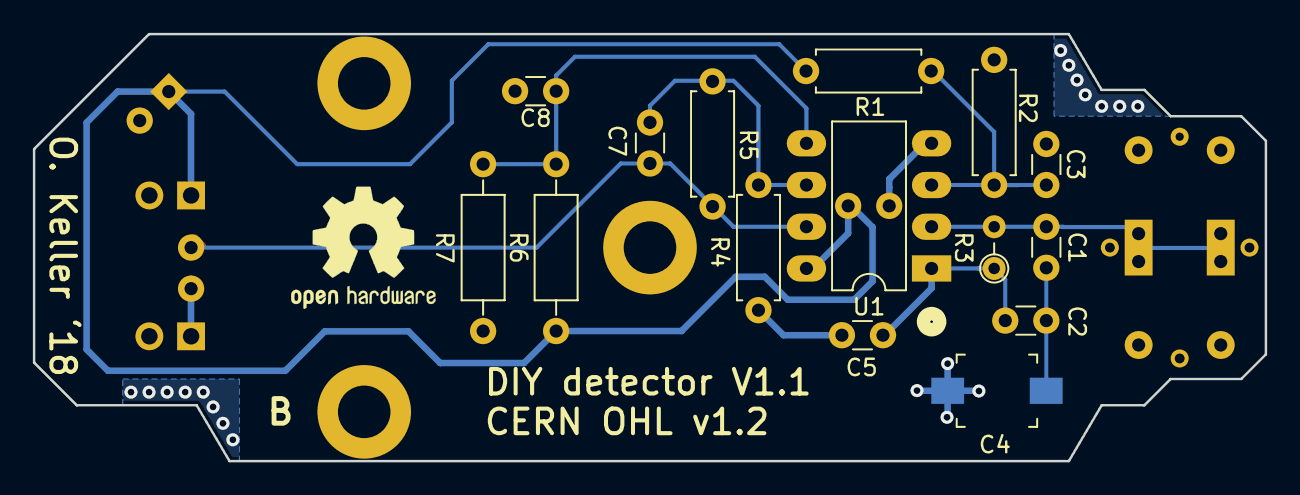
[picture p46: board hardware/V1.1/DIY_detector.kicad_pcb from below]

Board: 2 copper layers, 75.0 x 26.0 mm, 31 parts (15 on the bottom side), 11 nets.

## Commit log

2019-08-05 Initial commit Includes HW versions V1.1 and V1.2, released here under the CERN OHL License V 1.2 All software sources released here under the BSD License
    [# C-V Oliver [BPW34-1(1) _C-V Temp 20C 1MHz_; 3_1_2019 10_24_29 AM].csv, # C-V Oliver [BPW34-2(1) _C-V Temp 20C 1MHz_; 3_1_2019 3_29_29 PM].csv, # C-V Oliver [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]
2019-08-06 update BPX61 orientation in renderings
    [DIY_detector.kicad_pcb]
2019-08-07 adding gerber files
    [DIY_detector-B_Cu.gbl, DIY_detector-B_Mask.gbs, DIY_detector-B_Paste.gbp, DIY_detector-B_SilkS.gbo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]
2019-12-29 embedding small artwork in front copper layer
    [DIY_detector.kicad_pcb]
2019-12-29 adding green highlight marker for calibration purposes
    vertical position can be controlled via keypad in fine and coarse steps
    also improved sonification
2019-12-29 updating documentation and new parts overview sheets for assembly
    updating PDF of schematic, gerber files of board layout, and fixing some typos as well
    [DIY_detector-B_Cu.gbl, DIY_detector-B_Mask.gbs, DIY_detector-B_Paste.gbp, DIY_detector-B_SilkS.gbo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]
2019-12-29 simplified description about the two variants
    adding new parts overview sheets and link to the updated schematic, referenced the article corresponding to this repo which was pusblished in the Sensors magazine
2020-01-01 BOM files in preparation for Kitspace release
    [1-click-bom_alpha-spectrometer.csv, 1-click-bom_electron-detector.csv, DIY_detector.kicad_pcb, DIY_detector.sch]
2020-01-17 renderings and 3D part models for both variants
    including generated 3D models for all THT resistors, opamp chip model
    with label. also created more accurate BPX61 TO-39 model.
    Schematic and exported .xml BOM file have two new columns which store
    part values and 3D model locations of the electron detector assembly
    variant (VALUE_B, 3D_B)
    [BPW34.FCStd, BPW34F.step, BPW_34_20180209_geometry.STEP, BPX61.FCStd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]
2020-01-21 BPX61 diode model without window
    improved parts overview pdf, added example oscilloscope plots of KCL
    (betas/gammas only) for both detector variants
    [BPX61.FCStd, DIY_detector.kicad_pcb]
2020-02-12 fixing Alpha-spectro kitspace bom
    removed D1-D3 which are not required in this version and add switch part
    reference of all four suppliers
    [1-click-bom_alpha-spectrometer.csv]
2020-02-12 updated electron-detector bom
    better reference for the BPW34 FA diode at Farnell with improved
    availability
    [1-click-bom_electron-detector.csv]
2020-02-12 better refs for Digikey BOMs
    [1-click-bom_alpha-spectrometer.csv, 1-click-bom_electron-detector.csv]
2020-06-21 picture of die-cast Al enclosures
2020-10-09 adding 2nd KiCAD pcb file for Kitspace's assembly guide
    DIY_detector_electron-variant.kicad_pcb shows the alternative part
    selection (values & 3D models). It is generated from VALUE_B and 3D_B
    fields in the schematic file which is the common base for both
    .kicad_pcb files.
    This new pcb design file is only for kitspace's assembly guide feature
    (interactive BOM).
    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
    [DIY_detector_electron-variant.kicad_pcb]
2020-10-09 updating part visibility
    set several footprints as virtual to prevent appearance in the
    interactive assembly guide
    [DIY_detector.kicad_pcb, DIY_detector_electron-variant.kicad_pcb]
2020-11-04 updating BOMs fxing part number for R5@Farnell and some house keeping
    [1-click-bom_alpha-spectrometer.csv, 1-click-bom_electron-detector.csv]

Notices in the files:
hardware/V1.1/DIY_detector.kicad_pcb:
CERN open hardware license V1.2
